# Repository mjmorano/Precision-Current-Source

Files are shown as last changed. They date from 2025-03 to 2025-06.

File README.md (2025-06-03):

# Overview
This is all of the design files and the code needed for my precision current source. The code for the microcontroller was made using the Arduino framework and PlatformIO so it's easy to modify and can be uploaded without neededing a programmer, just an Arduino. The serial interface features a few basic commands for setting the current and reading it back using the onboard ADC, as well as reading the internal temperature sensors. I added a lot of error checking to the firmware so it should be basically impossible to make the device do something that it shouldn't, and give the user feedback if their inputs are accepted or not. This design uses an external voltage source up to 100 volts, so it can be used with relatively high resistance loads. It is also suitable for high inductance loads, and has been verified stable into 250 mH. The KiCad folder contains all of the schematics and the .zip files with the gerbers needed to have the PCBs and the front panel manufactured. I have the front panels made as aluminum PCBs with no copper layers, which pretty much any manufacturer can do.

<p align="center">
  
  
  
</p>

# Stability Measurement
Since this is meant to be used for driving gradient and shim coils for long experimental runs, temperature stability is critical. To measure the stability I rented a Keysight 3458A and logged data for a week at maximum output current and the result can be seen in the plot below. Allan deviations for this data are also shown. The current stability could be further improved by using a different voltage reference, the LTZ1000A or LM399 for example, but these would come with a significant accuracy penalty. Of course the accuracy can be calibrated in software, but that requires the user to have a very good DMM and makes the assembly process more complicated. I tried to balance initial accuracy and temperature stability as much as possible.

<p align="center">
  
  
</p>

# Flashing the Firmware
To upload the program to the microcontroller, the Arduino bootloader needs to be burned. It's possible to buy the microcontroller with the bootloader already installed, but it's easy to do yourself. The best way to do this is in the Arduino IDE, and I'll outline how to do it with either an Uno or a Nano. First the ArduinoISP sketch needs to be uploaded to Arduino and can be found under the example sketches as shown below.

<p align="center">
 
</p>

Once it's uploaded connect the Arduino pins to the 6 pin header on the current source as follows:

  | Arduino | Current Source |
  |:-------:|:--------------:|
  |    10   |    RESET       |
  |    11   |    MOSI        |
  |    12   |    MISO        |
  |    13   |    SCK         |
  |    5V   |    5V          |
  |   GND   |    GND         |

Next under tools set the programmer to be "Arduino as ISP", then click burn bootloader. If everything is working right a message should pop up in the bottom right corner of the Arduino IDE saying "Burning bootloader...", followed by a message saying "Done burning bootloader."
<p align="center">
  
  
  
</p>

Now that the bootloader is burned open the Code/Microcontroller folder from the repo in VS Code, making sure to have the PlatformIO extension installed. After PlatformIO initializes select the port for the Arduino that was used to burn the bootloader in the bottom left, for me it was COM5.
<p align="center">
  
</p>

After this all that needs to be done is to click the upload button and the terminal should look like the below image.
<p align="center">
  
  
</p>

Now the device is ready to be connected over USB to a computer.

# Serial Interface
When the device is connected to the computer it should show up as a COM port in windows and a ttyUSB device on Linux. On Linux the device will need to be chmodded in order to connect to it using pyserial. Usually the FTDI drivers automatically download or are already installed, but if not they can be downloaded [here](https://ftdichip.com/drivers/vcp-drivers/). The interface uses eight data bits, no parity, and one stop bit at 115200 baud. On powerup the device does some self checks and looks to see if the optional tmp117 temperature sensor is present. After connecting to the serial interface two readlines need to be done, the first says whether the tmp117 is detected or not, and the second is for any detected errors. If the device detects no errors the second readline will return "Ready." Examples of how to use pyserial with the device are shown in the Code/Serial_Interface_Examples.py file. There are some other commands not shown there, but they won't really be used.

# Schematics
[Precision Current Source.pdf](https://github.com/user-attachments/files/20560946/Precision.Current.Source.pdf)

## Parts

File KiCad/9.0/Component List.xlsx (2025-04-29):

Item | Qty | Reference(s) | Value | Footprint | Digikey Part # | Manufacturer part #
1 | 3 | C201, C204, C213 | 10u 100V | SMD 6.3x7.7 | 732-865060845002CT-ND | 865061000000
2 | 15 | C202, C208, C209, C210, C211, C212, C302, C305, C306, C309, C310, C311, C312, C313, C314 | 100n 50V X7R | 0603 | 399-C0603C104K5RACTUCT-ND | C0603C104K5RACTU
3 | 10 | C203, C301, C401, C402, C403, C404, C405, C406, C407, C408 | 47u 35V | SMD 6.3x5.5 | 732-8508-1-ND | 865081000000
4 | 2 | C205, C207 | 100p 50V C0G | 0603 | 490-1427-1-ND | GRM1885C1H101JA01D
5 | 1 | C206 | 1u 100V Film | 2824 | 478-4539-1-ND | CB052E0105JBC
6 | 2 | C307, C308 | 20p 50V C0G | 0603 | 1276-1187-1-ND | CL10C200JB8NNNC
7 | 8 | D201, D202, D401, D402, D403, D404, D405, D406 | Schottky 40V | SOD-123F | B140S1F-7 | 31-B140S1F-7CT-ND
8 | 2 | D301, D302 | Dual LED | WP934MD | 754-2010-ND | WP934MD/LILGD
9 | 1 | F201 | Fuse Holder | 0031.7701.22 | 486-3856-1-ND | 0031.7701.22
10 | 1 | FB301 | 120 | 0603 | 490-5254-1-ND | BLM18KG121TN1D
11 | 1 | HS201 | 6396BG | 6396BG | 6396BG-ND | 6396BG
12 | 1 | HS202 | Heatsink | 577102B04000G | HS368-ND | 577102B04000G
13 | 1 | J201, J202, J203, J204 | Tab Connector | Through Hole | 36-1211-ND | 1211
14 | 1 | J301 | 6 Pin Header | 2x3 2.54 Through Hole | 952-2121-ND | M20-9980346
15 | 1 | J302 | USB B | Through Hole Right Angle | 102-3999-ND | UJ2-BH-1-TH
16 | 1 | Q201 | IRF510 | TO-220-3 | IRF510PBF-ND | IRF510PBF
17 | 1 | Q401 | FMMT614TA | SOT-23-3 | FMMT614CT-ND | FMMT614TA
18 | 1 | Q402 | FMMT734 | SOT-23-3 | FMMT734CT-ND | FMMT734TA
19 | 1 | R201 | 10K | 0603 | RMCF0603JT10K0CT-ND | RMCF0603JT10K0
20 | 6 | R202, R203, R303, R304, R305, R306 | 1k | 0603 | RMCF0603FT1K00CT-ND | RMCF0603FT1K00
21 | 1 | R204 | 10R | TO-220-4 | Y0926-10A-ND | Y092610R0000T9L
22 | 2 | R401, R402 | 160 | 603 | 311-160GRCT-ND | RC0603JR-07160RL
23 | 3 | RN301, RN302, RN303 | 4x1k | 4x0603 | 60-742C083102JPCT-ND | 742C083102JP
24 | 1 | RN304 | 4x120 | 4x0603 | Y4121CT-ND | EXB-V8V121JV
25 | 1 | S101 | RF Shield Frame | 32x32 | 903-BMI-S-204-FCT-ND | BMI-S-204-F
26 | 2 | TH301, TH302 | 1k NTC | Through Hole | 900-2152723107-ND | 2152723107
27 | 1 | U201 | ADR441B | SOIC-8 | 505-ADR441BRZ-ND | ADR441BRZ
28 | 1 | U202 | LTC1595B | SOIC-8 | LTC1595BCS8#TRPBFCT-ND | LTC1595BCS8#TRPBF
29 | 1 | U203 | OPA4182 | SOIC-14 | 296-OPA4182IDRCT-ND | OPA4182IDR
30 | 1 | U204 | AD7789 | MSOP-10 | AD7789BRMZ-REELCT-ND | AD7789BRMZ-REEL
31 | 1 | U205 | 4x1k | SOIC-8 | ORNT-1KACT-ND | ORNTA1001AT1
32 | 1 | U301 | FT231XS-U | SSOP-10 | 768-1156-5-ND | FT231XS-U
33 | 1 | U302 | ATMEGA328P | TQFP-32 | ATMEGA328P-AU-ND | ATMEGA328P-AU
34 | 1 | U303 | ADuM261N0 | SOIC-16 7.5W | 505-ADUM261N0BRIZ-ND | ADUM261N0BRIZ
35 | 1 | U304 | TMP117xxDRV | WSON-6 | 296-51835-1-ND | TMP117MAIDRVR
36 | 1 | U401 | L78L15 | SOT-89-3 | 497-7769-1-ND | L78L15ABUTR
37 | 1 | U402 | PESE1-S5-S24-M | SMD-10 Module | PESE1-S5-D24-M-TR | PESE1-S5-D24-M-TR
38 | 1 | U403 | L78L05 | SOT-89-3 | 497-1181-1-ND | L78L05ABUTR
39 | 1 | U404 | L79L15 | SOT-89-3 | 497-L79L15ACUCT-ND | L79L15ACUTR
40 | 1 | Y301 | 16 MHz | HC-49/US | XC1776CT-ND | ECS-160-20-3X-TR
Mechanical Parts
Item | Qty | Description | Digikey Part # | Manufacturer Part #
1 | 1 | RF Shield Cover | 903-1016-ND | BMI-S-204-C
2 | 1 | Terminal Block Header | 277-5988-ND | 707264
3 | 1 | Terminal Block | 277-1013-ND | 1757035
4 | 2 | Terminal Block Mounting Screw | 277-5786-ND | 708263
5 | 1 | Enclosure | HM972-ND | 1455K1201
6 | 8 | Crimp Connector | 277-17467-ND | 3240535
7 | 8 | 6-32x3/8" Screw | PMS 632 0038 PH | H356-ND
8 | 1 | 350 mA Fast Blow Fuse | 486-3000-ND | 3404.0043.11

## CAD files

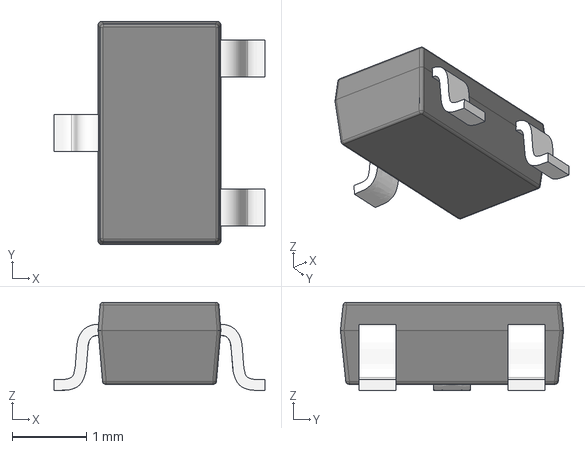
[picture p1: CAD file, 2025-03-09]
KiCad/9.0/3D Models/SOT23-3.stp
2.84 x 3.00 x 1.18 mm

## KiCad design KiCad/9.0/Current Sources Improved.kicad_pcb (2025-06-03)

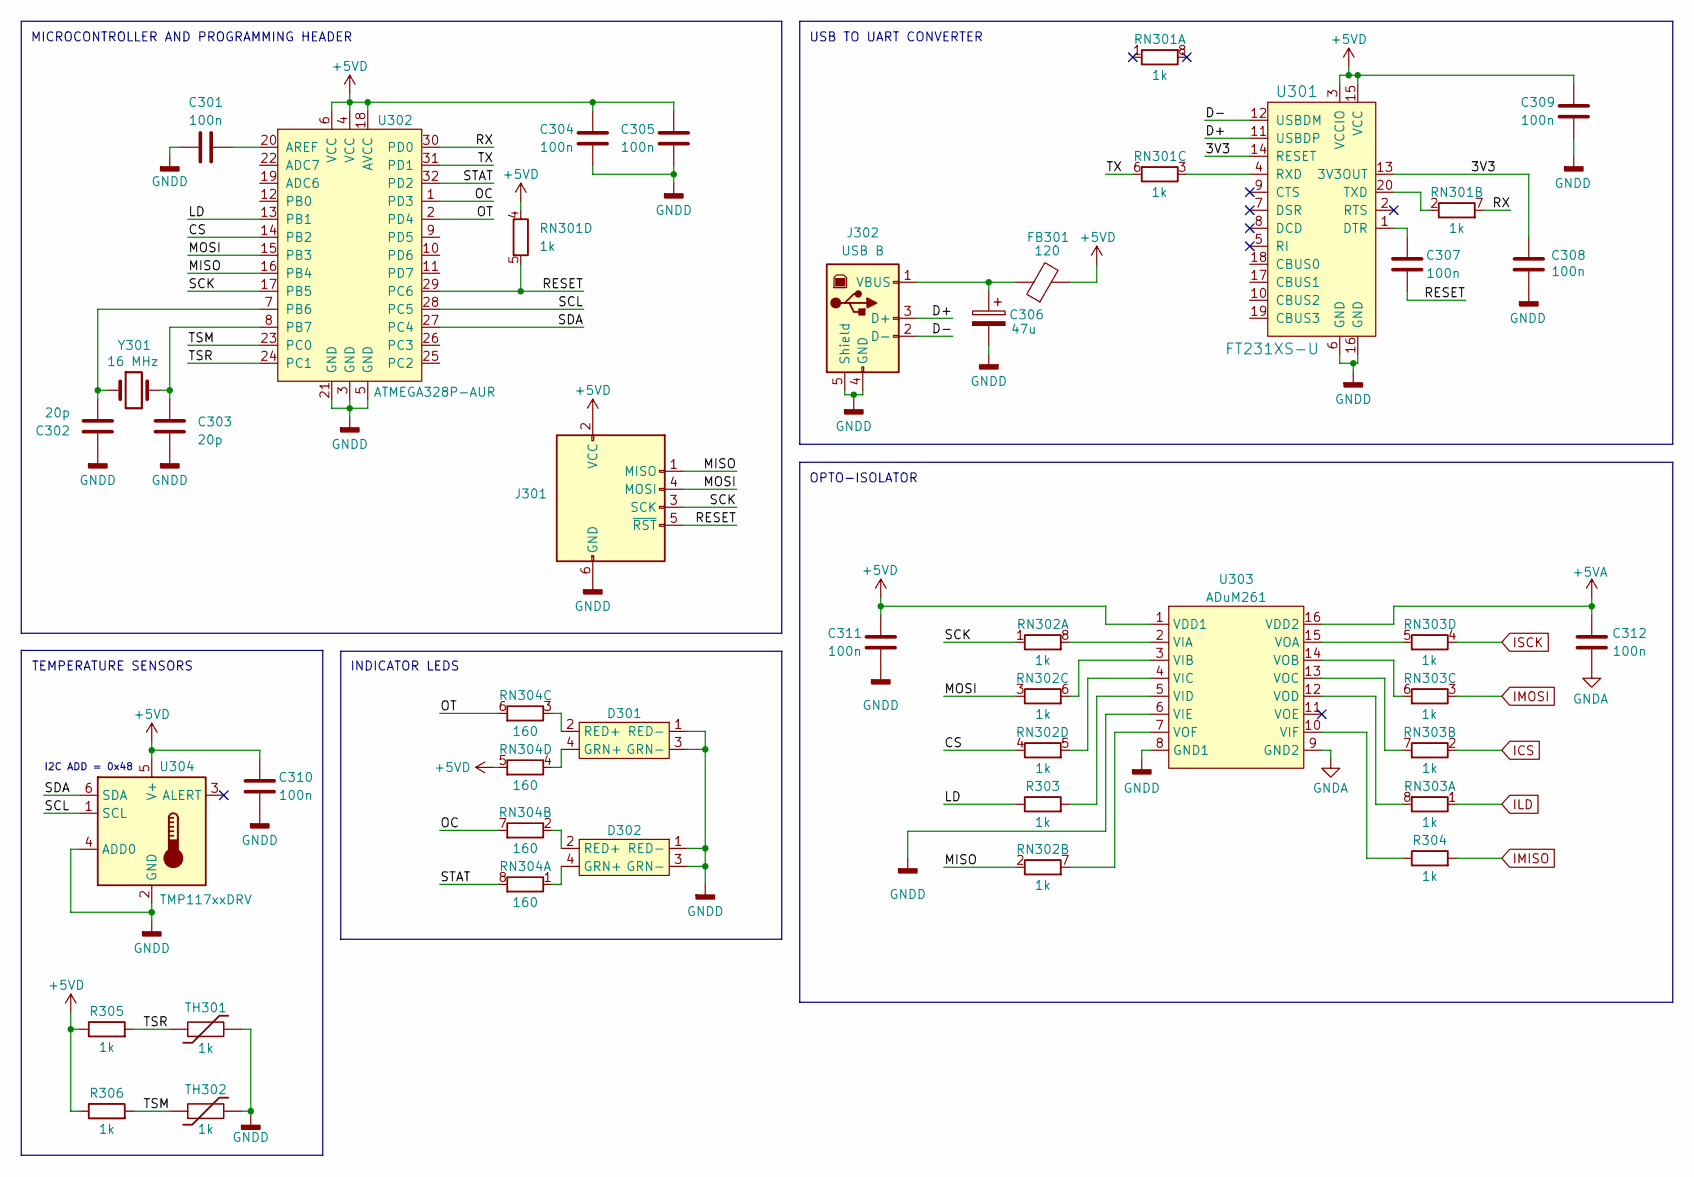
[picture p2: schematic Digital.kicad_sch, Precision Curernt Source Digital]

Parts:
C301, C304, C305, C307, C308, C309, C310, C311, C312: 100n; C_0603_1608Metric
C302, C303: 20p; C_0603_1608Metric
C306: 47u; CP_Elec_6.3x5.8
D301, D302: WP934MD
FB301: 120; R_0603_1608Metric
J301: AVR-ISP-6; PinHeader_2x03_P2.54mm_Vertical
J302: USB B; UJ2-BH-1-TH_CUD
R303, R304, R305, R306: 1k; R_0603_1608Metric
RN301, RN302, RN303: 1k; R_Array_Concave_4x0603
RN304: 160; R_Array_Concave_4x0603
TH301, TH302: 1k; PinHeader_1x02_P2.54mm_Vertical
U301: FT231XS-U; SSOP-20_W3.9mm; MPN FT231XS-U; Digi-Key_PN 768-1156-5-ND
U302: ATMEGA328P-AUR; TQFP-32_7x7mm; MPN ATMEGA328P-AUR; Digi-Key_PN ATMEGA328P-AURCT-ND
U303: ADuM261; SOIC-16W_7.5x12.8mm_P1.27mm
U304: TMP117xxDRV; WSON-6-1EP_2x2mm_P0.65mm_EP1x1.6mm
Y301: 16 MHz; XTAL_ECS-200-20-3X-TR

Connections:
+5VA: C312.2, U303.16 (VDD2); also elsewhere on the board
+5VD: C304.1, C305.2, C309.2, C310.1, C311.2, FB301.2, J301.2 (VCC), R305.1, R306.1, RN301.4 (R4.1), RN304.5 (R4.2), U301.3 (VCCIO), U301.15 (VCC), U302.4 (VCC), U302.6 (VCC), U302.18 (AVCC), U303.1 (VDD1), U304.5 (V+); also elsewhere on the board
/Digital/3V3: C308.1, U301.13 (3V3OUT), U301.14 (RESET)
/Digital/CS: RN302.4 (R4.1), U302.14 (PB2)
/Digital/D+: J302.3 (D+), U301.11 (USBDP)
/Digital/D-: J302.2 (D-), U301.12 (USBDM)
/Digital/LD: R303.1, U302.13 (PB1)
/Digital/MISO: J301.1 (MISO), RN302.2 (R2.1), U302.16 (PB4)
/Digital/MOSI: J301.4 (MOSI), RN302.3 (R3.1), U302.15 (PB3)
/Digital/OC: RN304.7 (R2.2), U302.1 (PD3)
/Digital/OT: RN304.6 (R3.2), U302.2 (PD4)
/Digital/RESET: C307.1, J301.5 (~RST), RN301.5 (R4.2), U302.29 (PC6)
/Digital/RX: RN301.7 (R2.2), U302.30 (PD0)
/Digital/SCK: J301.3 (SCK), RN302.1 (R1.1), U302.17 (PB5)
/Digital/SCL: U302.28 (PC5), U304.1 (SCL)
/Digital/SDA: U302.27 (PC4), U304.6 (SDA)
/Digital/STAT: RN304.8 (R1.2), U302.32 (PD2)
/Digital/TSM: R306.2, TH302.1, U302.23 (PC0)
/Digital/TSR: R305.2, TH301.1, U302.24 (PC1)
/Digital/TX: RN301.6 (R3.2), U302.31 (PD1)
GNDA: C312.1, U303.9 (GND2); also elsewhere on the board
GNDD: C301.2, C302.1, C303.2, C304.2, C305.1, C306.2, C308.2, C309.1, C310.2, C311.1, D301.1 (RED-), D301.3 (GRN-), D302.1 (RED-), D302.3 (GRN-), J301.6 (GND), J302.4 (GND), J302.5 (Shield), TH301.2, TH302.2, U301.6 (GND), U301.16 (GND), U302.3 (GND), U302.5 (GND), U302.21 (GND), U303.6 (VIE), U303.8 (GND1), U304.2 (GND), U304.4 (ADD0); also elsewhere on the board
ICS: RN303.2 (R2.1); also elsewhere on the board
ILD: RN303.1 (R1.1); also elsewhere on the board
IMISO: R304.2; also elsewhere on the board
IMOSI: RN303.3 (R3.1); also elsewhere on the board
ISCK: RN303.4 (R4.1); also elsewhere on the board
unnamed: D301.4 (GRN+), RN304.4 (R4.1)
unnamed: D301.2 (RED+), RN304.3 (R3.1)
unnamed: D302.4 (GRN+), RN304.1 (R1.1)
unnamed: D302.2 (RED+), RN304.2 (R2.1)
unnamed: C306.1, FB301.1, J302.1 (VBUS)
unnamed: RN301.2 (R2.1), U301.20 (TXD)
unnamed: RN301.3 (R3.1), U301.4 (RXD)
unnamed: RN302.8 (R1.2), U303.2 (VIA)
unnamed: RN302.7 (R2.2), U303.7 (VOF)
unnamed: RN302.6 (R3.2), U303.3 (VIB)
unnamed: RN302.5 (R4.2), U303.4 (VIC)
unnamed: RN303.8 (R1.2), U303.12 (VOD)
unnamed: RN303.7 (R2.2), U303.13 (VOC)
unnamed: RN303.6 (R3.2), U303.14 (VOB)
unnamed: RN303.5 (R4.2), U303.15 (VOA)
unnamed: C307.2, U301.1 (DTR)
unnamed: C301.1, U302.20 (AREF)
unnamed: C302.2, U302.7 (PB6), Y301.1
unnamed: C303.1, U302.8 (PB7), Y301.2
unnamed: R303.2, U303.5 (VID)
unnamed: R304.1, U303.10 (VIF)

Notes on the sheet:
MICROCONTROLLER AND PROGRAMMING HEADER
TEMPERATURE SENSORS
INDICATOR LEDS
USB TO UART CONVERTER
I2C ADD = 0x48
OPTO-ISOLATOR

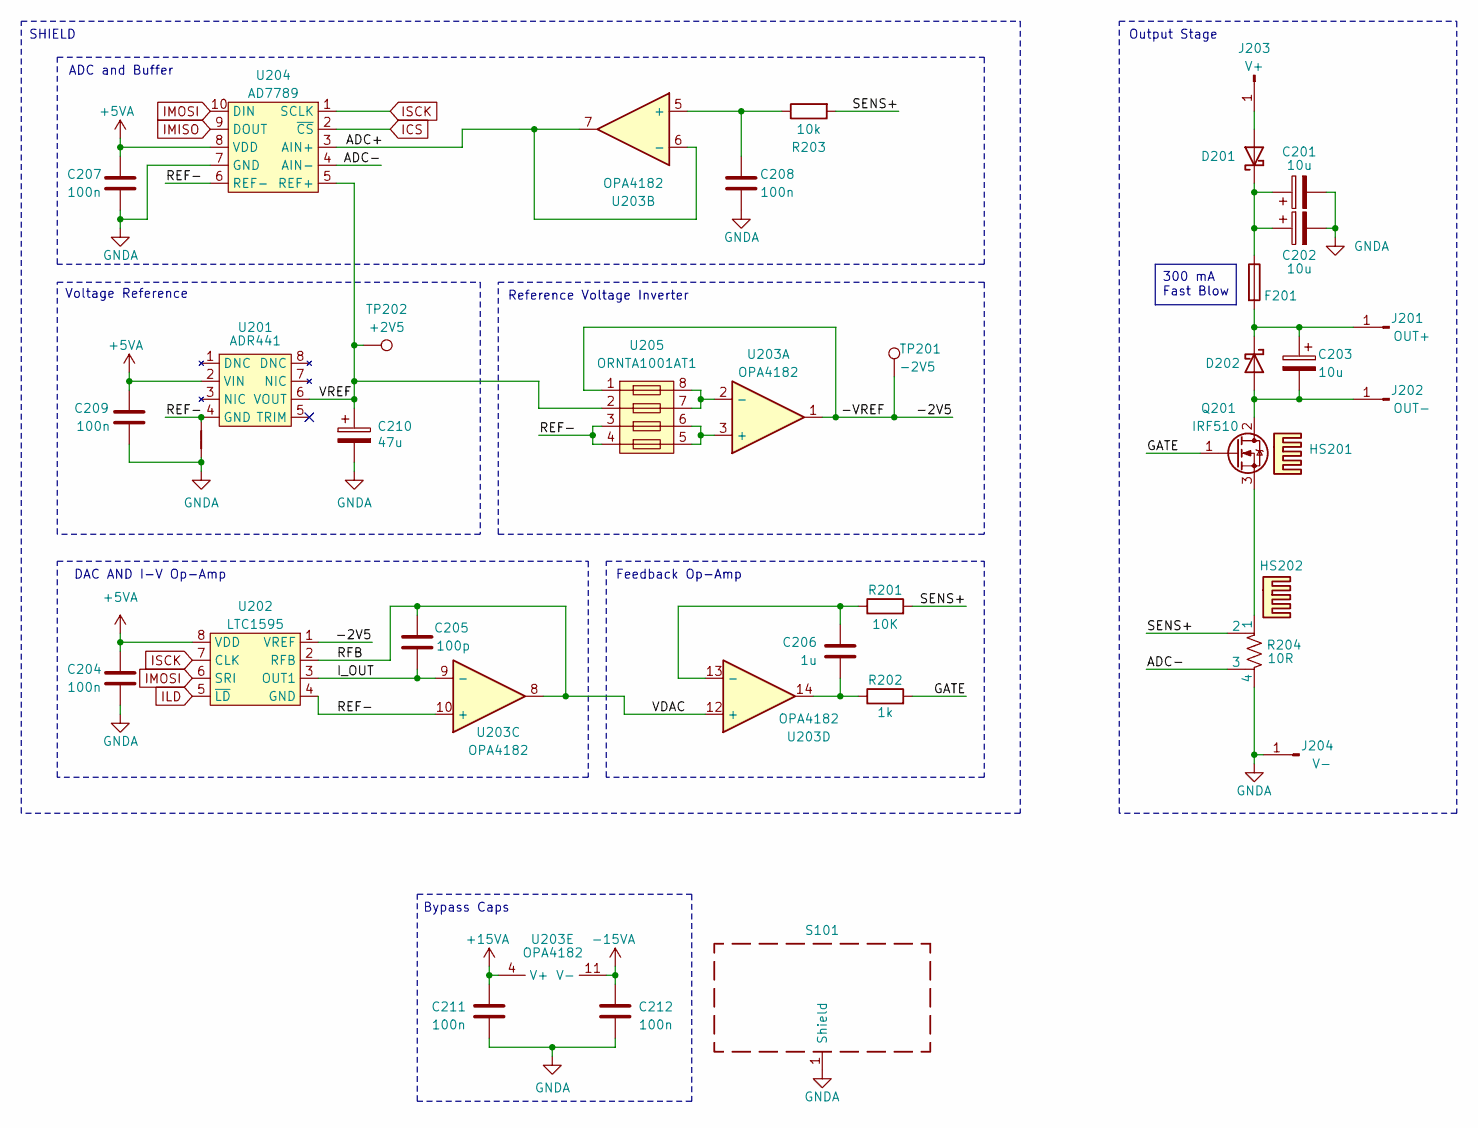
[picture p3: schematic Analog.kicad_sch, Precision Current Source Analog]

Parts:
C201, C202, C203: 10u; CP_Elec_6.3x5.8
C204, C207, C208, C209, C211, C212: 100n; C_0603_1608Metric
C205: 100p; C_0603_1608Metric
C206: 1u; CB05_AVX
C210: 47u; CP_Elec_6.3x5.8
D201, D202: D_Schottky; D_SOD-123F
F201: Fuse; 0031.7701.22
HS201: 530002B02500G; 529802B02500G; Mouser Part Number 532-530002B02500G
HS202: Heatsink; 577102B04000G
J201: OUT+; 1211
J202: OUT-; 1211
J203: V+; 1211
J204: V-; 1211
NT201: NetTie_2; SmallNetTie
Q201: IRF510; TO-220-3_Vertical
R201: 10K; R_0603_1608Metric
R202: 1k; R_0603_1608Metric
R203: 10k; R_0603_1608Metric
R204: 10R; TO-220-4_Vertical
S101: RFShield_OnePiece; Laird_Technologies_BMI-S-204-F_32.00x32.00mm
TP201: -2V5; TestPoint_Pad_D1.0mm
TP202: +2V5; TestPoint_Pad_D1.0mm
U201: ADR441; SOIC-8_3.9x4.9mm_P1.27mm
U202: LTC1595; SOIC-8_3.9x4.9mm_P1.27mm
U203: OPA4182; SOIC-14_3.9x8.7mm_P1.27mm
U204: AD7789; MSOP-10_3x3mm_P0.5mm
U205: ORNTA1001AT1; SOIC-8_3.9x4.9mm_P1.27mm

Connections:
+5VA: C204.1, C207.1, C209.1, U201.2 (VIN), U202.8 (VDD), U204.8 (VDD); also elsewhere on the board
+15VA: C211.2, U203.4 (V+); also elsewhere on the board
-15VA: C212.2, U203.11 (V-); also elsewhere on the board
/Analog/-2V5: TP201.1, U202.1 (VREF), U203.1, U205.1
/Analog/ADC+: U203.6 (-), U203.7, U204.3 (AIN+)
/Analog/ADC-: R204.3, U204.4 (AIN-)
/Analog/GATE: Q201.1 (G), R202.2
/Analog/I_OUT: C205.2, U202.3 (OUT1), U203.9 (-)
/Analog/REF-: NT201.2, U201.4 (GND), U202.4 (GND), U203.10 (+), U204.6 (REF-), U205.3, U205.4
/Analog/RFB: C205.1, U202.2 (RFB), U203.8, U203.12 (+)
/Analog/SENS+: R201.2, R203.2, R204.2
/Analog/VREF: C210.1, TP202.1, U201.6 (VOUT), U204.5 (REF+), U205.2
GNDA: C201.2, C202.2, C204.2, C207.2, C208.2, C209.2, C210.2, C211.1, C212.1, J204.1, NT201.1, R204.4, S101.1 (Shield), U204.7 (GND); also elsewhere on the board
ICS: U204.2 (~CS); also elsewhere on the board
ILD: U202.5 (~LD); also elsewhere on the board
IMISO: U204.9 (DOUT); also elsewhere on the board
IMOSI: U202.6 (SRI), U204.10 (DIN); also elsewhere on the board
ISCK: U202.7 (CLK), U204.1 (SCLK); also elsewhere on the board
unnamed 40: C206.2, R202.1, U203.14; also elsewhere on the board
unnamed: D201.2 (A), J203.1
unnamed: C201.1, C202.1, D201.1 (K), F201.1
unnamed: C203.2, D202.2 (A), J202.1, Q201.2 (D)
unnamed: C203.1, D202.1 (K), F201.2, J201.1
unnamed: Q201.3 (S), R204.1
unnamed: U203.3 (+), U205.5, U205.6
unnamed: U203.2 (-), U205.7, U205.8
unnamed: C208.1, R203.1, U203.5 (+)
unnamed 68: C206.1, R201.1, U203.13 (-); also elsewhere on the board

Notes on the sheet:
ADC and Buffer
SHIELD
Reference Voltage Inverter
Feedback Op-Amp
Voltage Reference
DAC AND I-V Op-Amp
Output Stage
Bypass Caps
300 mA Fast Blow

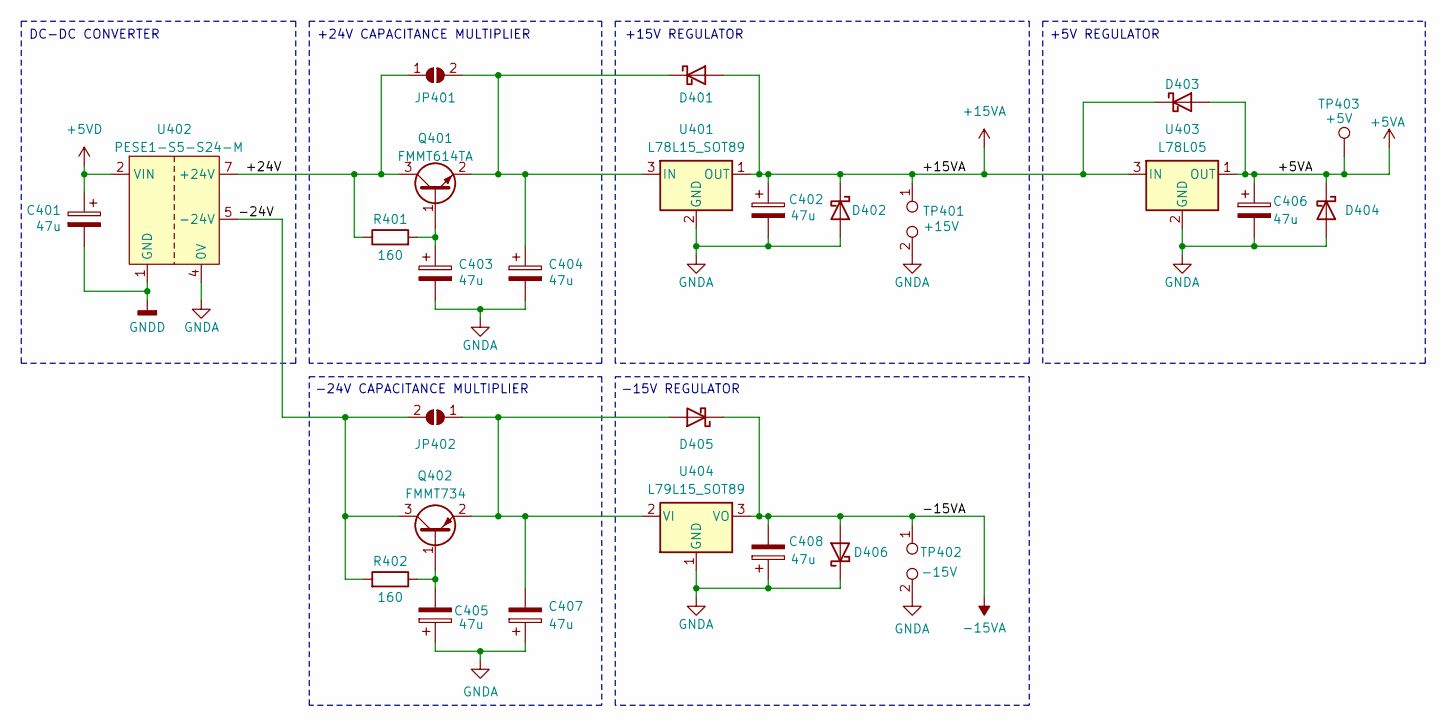
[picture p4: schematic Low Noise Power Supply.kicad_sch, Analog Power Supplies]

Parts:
C401, C402, C403, C404, C405, C406, C407, C408: 47u; CP_Elec_6.3x5.8
D401, D402, D403, D404, D405, D406: D_Schottky; D_SOD-123F
JP401, JP402: SolderJumper_2_Open; SolderJumper-2_P1.3mm_Open_RoundedPad1.0x1.5mm
Q401: FMMT614TA; SOT-23-3
Q402: FMMT734; SOT-23-3
R401, R402: 160; R_0603_1608Metric
TP401: +15V; testPoint2Pads
TP402: -15V; testPoint2Pads
TP403: +5V; TestPoint_Pad_D1.0mm
U401: L78L15_SOT89; SOT-89-3
U402: PESE1-S5-S24-M; PDS1-S5-D15-M-TR
U403: L78L05; SOT-89-3
U404: L79L15_SOT89; SOT-89-3

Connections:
+5VA: C406.1, D403.2 (A), D404.1 (K), TP403.1, U403.1 (OUT); also elsewhere on the board
+5VD: C401.1, U402.2 (VIN); also elsewhere on the board
+15VA: C402.1, D401.2 (A), D402.1 (K), D403.1 (K), TP401.1, U401.1 (OUT), U403.3 (IN); also elsewhere on the board
-15VA: C408.2, D405.1 (K), D406.2 (A), TP402.1, U404.3 (VO); also elsewhere on the board
/POWER/+24V: JP401.1 (A), Q401.3 (C), R401.1, U402.7 (+24V)
/POWER/-24V: JP402.2 (B), Q402.3 (C), R402.2, U402.5 (-24V)
GNDA: C402.2, C403.2, C404.2, C405.1, C406.2, C407.1, C408.1, D402.2 (A), D404.2 (A), D406.1 (K), TP401.2, TP402.2, U401.2 (GND), U402.4 (0V), U403.2 (GND), U404.1 (GND); also elsewhere on the board
GNDD: C401.2, U402.1 (GND); also elsewhere on the board
unnamed: C404.1, D401.1 (K), JP401.2 (B), Q401.2 (E), U401.3 (IN)
unnamed: C407.2, D405.2 (A), JP402.1 (A), Q402.2 (E), U404.2 (VI)
unnamed: C403.1, Q401.1 (B), R401.2
unnamed: C405.2, Q402.1 (B), R402.1

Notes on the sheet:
-24V CAPACITANCE MULTIPLIER
+24V CAPACITANCE MULTIPLIER
+5V REGULATOR
-15V REGULATOR
DC-DC CONVERTER
+15V REGULATOR

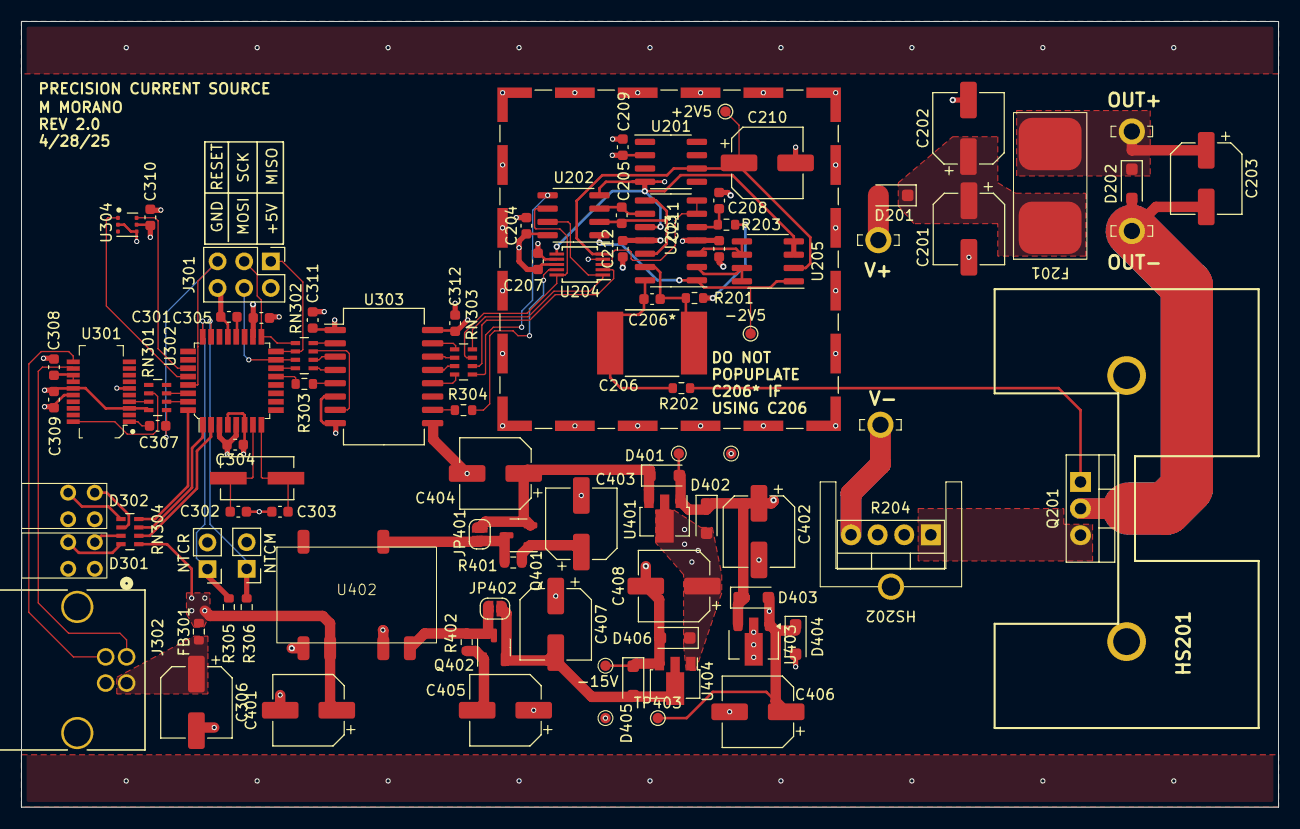
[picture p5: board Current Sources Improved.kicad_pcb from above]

Board: 4 copper layers, 120.0 x 75.0 mm, 95 parts (1 on the bottom side), 75 nets.

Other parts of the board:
C206*: C_0603_1608Metric

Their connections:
unnamed 40: C206*.1; also elsewhere on the board
unnamed 68: C206*.2; also elsewhere on the board

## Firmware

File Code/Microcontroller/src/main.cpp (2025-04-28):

/*
 * Code for the B0 and shim/gradient powIer supply. Uses an AD7789 ADC for current readback
 * and an LTC1595 based circuit for setting the output current. Uses a modified version of
 * the Analog Devices CN0216 circuit from the lab example for reading the ADC.
 * 
 * Author: M. Morano
 * Date: 4/25/2025
*/

#include <Arduino.h>
#include <SPI.h>
#include <Wire.h>
#include <Adafruit_TMP117.h>
#include <Adafruit_Sensor.h>
#include "AD7789.h"

// Do all the setup stuff
#define STAT 2      // Stats LED pin
#define OC 3        // Overcurrent LED pin
#define OT 4        // Overtemp LED pin
#define LD 9        // LD pin for the LTC1595
#define TSR A0      // Resistor NTC on ADC channel 0
#define TSM A1      // MOSFET NTC on ADC channel 1

const float maxAdcCode = pow(2, 24);        // Max code for 24 bit ADC
const float maxDacCode = pow(2, 16) - 1;    // Max code for 16 bit DAC
float R1 = 10.0f;                           // Current shunt resistor value. Change this if using different value
float vref = 2.5f;                          // ADC reference voltage
uint16_t code = 0;                          // Code for DAC current setpoint
float I = 0.0;                              // Current set value
uint32_t myTime = 0;                        // Used for polling the temperature sensors
uint8_t nAvg = 1;                           // Number of ADC averages
bool adcGood = false;

// Temperature sensor stuff
Adafruit_TMP117  tmp117;
sensors_event_t temp;
bool tmpFound = true;
float* Ta = &temp.temperature;
float Tr = 0.0f;                // NTC1 temperature reading
float Tm = 0.0f;                // NTC2 temperature reading
const float beta = 3892.0f;     // Beta value for NTC
float TaMax = 80.f;             // Maximum temperature for the enclosure before shutdown
float TrMax = 90.f;             // Maximum temperature for the feedback resistor before shutdown
float TmMax = 90.f;             // Maximum temperature for the MOSFET before shutdown

const char term = '\n';         // Terminator for serial interface

float read_ADC(){
  
  uint32_t reading = 0;
  uint32_t ui32status = 0;
  
  for(int i=0; i<nAvg; i++){
    
    ui32status = 0;
    
    do {
      ui32status = AD7789.readAD7789(STATUS_READ);
    } while (ui32status & 0x80);
    
    reading += AD7789.readAD7789(DATA_READ);
  }
  
  return ((float)reading / (float)nAvg) * vref / maxAdcCode / R1;
}

float read_ADC_VDD(){
  
  uint32_t reading = 0;
  uint32_t ui32status = 0;
    
  do {
    ui32status = AD7789.readAD7789(STATUS_READ_VDD);
  } while (ui32status & 0x80);
    
  reading += AD7789.readAD7789(DATA_READ);
  
  return 1.17f * 5.f * (float)reading / maxAdcCode;
}

void readTemps(){
  int sensorValue = analogRead(TSR);
  float RNTC = 1e3 / (1023.0 / sensorValue - 1);
  Tr = 1.f / ( 1.f / 298.15f + (1.f / beta) * (float)log(RNTC / 1e3f) ) - 273.25f; // Gives the temperature in celsius
  delay(1);
  sensorValue = analogRead(TSM);
  RNTC = 1e3 / (1023.0 / sensorValue - 1);
  Tm = 1.f / ( 1.f / 298.15f + (1.f / beta) * (float)log(RNTC / 1e3f) ) - 273.25f; // Gives the temperature in celsius
}

void writeDAC(uint16_t code){
  SPI.beginTransaction( SPISettings(1000000, MSBFIRST, SPI_MODE0) );
  SPI.transfer16(code);
  SPI.endTransaction();
  digitalWrite(LD, LOW);
  digitalWrite(LD, HIGH);
}

bool AD7789INIT(){
	AD7789.writeAD7789(RESET, 0xFF);		      // Resets the part for initial use
	delay(1000);
  AD7789.writeAD7789(COMM_WRITE_VDD, 0x00);
  AD7789.writeAD7789(MODE_WRITE_VDD, 0x06);	    // Mode register value (continuous conversion, unipolar input)
  float vdd = read_ADC_VDD();
  AD7789.writeAD7789(COMM_WRITE, 0x00);
  if(vdd >= 4.75f && vdd <= 5.25f)
    return true;
  else
    return false;
}

void parseCmd(String inString){

  int8_t index = inString.indexOf('?');

  if (index == -1){
    index = inString.indexOf('=');

    if (index == -1)
      Serial.println("Invalid syntax");

    else {
      char cmd[10];
      char value[10];
      char* end;
      sscanf(inString.c_str(), "%[^=]=%s", cmd, value);

      if (!strcmp(cmd, "code")){
        int32_t inInt = strtol(value, &end, 10);

        if (isControl(*end)){
          if (inInt >= 0 && inInt <= 65535){
            code = (uint16_t)inInt;
            writeDAC(code);
            Serial.println("Ok");

          } else
            Serial.println("Code must be between 0 and 65535");

        } else
          Serial.println("Invalid Code");

      } else if (!strcmp(cmd, "nAvg")){        
        int32_t inInt = strtol(value, &end, 10);       

        if (isControl(*end)){
          if (inInt >= 1 && inInt <= 255){
            nAvg = (uint8_t)inInt;
            Serial.println("Ok");

          } else 
            Serial.println("nAvg must be between 1 and 255");

        } else
            Serial.println("Invalid number");

      } else if (!strcmp(cmd, "curr")){
        float I = (float)strtod(value, &end);

        if (isControl(*end)){          
          if (I >= 0.f && I <= 0.25f){
            code = (uint16_t)(maxDacCode * R1 * I / vref);
            writeDAC(code);
            Serial.println("Ok");

          } else 
            Serial.println("Current must be between 0 and 250mA");

        } else 
          Serial.println("Invalid number");

      } else if (!strcmp(cmd, "TrMax")){        
        float limit = (float)strtod(value, &end);       

        if (isControl(*end)){
          if (limit >= 0.f && limit <= 100.f){
            TrMax = limit;
            Serial.println("Ok");

          } else 
            Serial.println("TrMax must be between 0 and 100 C");

        } else
            Serial.println("Invalid temperature");

      } else if (!strcmp(cmd, "TaMax")){        
        float limit = (float)strtod(value, &end);       

        if (isControl(*end)){
          if (limit >= 0.f && limit <= 100.f){
            TaMax = limit;
            Serial.println("Ok");

          } else 
            Serial.println("TaMax must be between 0 and 100 C");

        } else
            Serial.println("Invalid temperature");

      } else if (!strcmp(cmd, "TmMax")){        
        float limit = (float)strtod(value, &end);       

        if (isControl(*end)){
          if (limit >= 0.f && limit <= 100.f){
            TmMax = limit;
            Serial.println("Ok");

          } else 
            Serial.println("TmMax must be between 0 and 100 C");

        } else
            Serial.println("Invalid temperature");

      } else
        Serial.println("Invalid command");

    }

  } else {

    char cmd[10];
    sscanf(inString.c_str(), "%[^?]?", cmd);

    if (!strcmp(cmd, "max")){      
      Serial.println("250 mA");

    } else if (!strcmp(cmd, "curr")){
      Serial.println(read_ADC(), 7);

    } else if (!strcmp(cmd, "TaMax")){
      Serial.println(TaMax, 2);

    } else if (!strcmp(cmd, "TrMax")){
      Serial.println(TrMax, 2);

    } else if (!strcmp(cmd, "TmMax")){
      Serial.println(TmMax, 2);

    } else if (!strcmp(cmd, "Tr")){
      Serial.println(Tr, 2);

    } else if (!strcmp(cmd, "Tm")){
      Serial.println(Tm, 2);

    } else if (!strcmp(cmd, "Ta")){
      Serial.println(*Ta, 2);

    } else if (!strcmp(cmd, "code")){
      Serial.println(code);

    } else if (!strcmp(cmd, "nAvg")){
      Serial.println(nAvg);

    } else if(!strcmp(cmd, "ID")){
      Serial.println("Precision current source");

    } else if(!strcmp(cmd, "temp")){
      if (tmpFound){
        tmp117.getEvent(&temp);
        Serial.print(*Ta, 2);
        Serial.print(", ");
      }
      Serial.print(Tr, 2);
      Serial.print(", ");
      Serial.println(Tm, 2);

    } else if(!strcmp(cmd, "Vdd")){
      AD7789.writeAD7789(COMM_WRITE_VDD, 0x00);
      AD7789.writeAD7789(MODE_WRITE_VDD, 0x06);	    // Mode register value (continuous conversion, unipolar input)
      float vdd = read_ADC_VDD();
      Serial.println(vdd, 7);
      AD7789.writeAD7789(COMM_WRITE, 0x00);

    } else if(!strcmp(cmd, "adc")){
      adcGood = AD7789INIT();
      if (adcGood)
        Serial.println("Good");
      else
        Serial.println("Bad");

    } else 
      Serial.println("Invalid query");

  }

}

void errorState(){
  while (1)
  {
    digitalWrite(STAT, HIGH);
    delay(250);
    digitalWrite(STAT, LOW);
    delay(250);
  }
}

void setup(){
	
  // open digital communication protocols
  Serial.begin(115200);
  Serial.setTimeout(50);
  SPI.begin();

  // initialize pins
  pinMode(OT, OUTPUT);
  digitalWrite(OT, LOW);
  pinMode(OC, OUTPUT);
  digitalWrite(OC, LOW);
  pinMode(STAT, OUTPUT);
  digitalWrite(STAT, LOW);       
  digitalWrite(SS, HIGH);		  
  pinMode(LD, OUTPUT);                
  digitalWrite(LD, HIGH);
  
  writeDAC(0);

  if (!tmp117.begin()) {
    Serial.println("Failed to find TMP117 chip");
    tmpFound = false;
    temp.temperature = 0.f;
  } else {
    Serial.println("TMP117 Found");
    tmp117.getEvent(&temp);
  }

  // initialize AD7791
  adcGood = AD7789INIT();

  // Read NTC temperature sensors
  readTemps();

  if (adcGood && Tr < TrMax && Tm < TmMax && *Ta < TaMax){
    Serial.println("Ready.");
    digitalWrite(STAT, HIGH);

  } else if (!adcGood){
    Serial.println("Error: Check ADC or power supply.");
    digitalWrite(OT, HIGH);
    digitalWrite(OC, HIGH);
    errorState();

  } else if (Tr >= TrMax){
    Serial.println("Error: R1 overtemp at startup.");
    digitalWrite(OT, HIGH);
    errorState();

  } else if (Tm >= TmMax){
    Serial.println("Error: MOSFET overtemp at startup.");
    digitalWrite(OT, HIGH);
    errorState();

  } else if (*Ta > TaMax){
    Serial.println("Error: Ambient overtemp at startup.");
    digitalWrite(OT, HIGH);
    errorState();

  } else {
    Serial.println("Error: ");
    errorState();

  }

  myTime = millis();

}

void loop(){

  if (millis() >= myTime + 500UL){
    readTemps();
    if (tmpFound)
      tmp117.getEvent(&temp);
    else
      temp.temperature = 0.f;

    if (Tr >= TrMax || Tm >= TmMax || *Ta >= TaMax){
      writeDAC(0);
      digitalWrite(OT, HIGH);
      errorState();
    }
    myTime = millis();

  }

  if (Serial.available()){
    String cmd = Serial.readStringUntil(term);

    if (cmd == "")
      Serial.println("Did you forget the \\n?");
    else
      parseCmd(cmd);
    
  }
}

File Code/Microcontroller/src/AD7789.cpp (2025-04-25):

/*
  AD7789.cpp - 
*/

#include <Arduino.h>
#include <SPI.h>
#include "AD7789.h"

AD7789class AD7789;

uint32_t AD7789class::readAD7789 (uint8_t ui8address){
	uint8_t ui8AdcUpperCodes = 0;			// Data register bits 23-16
	uint8_t ui8AdcMiddleCodes = 0;			// Data register bits 15-8
	uint8_t ui8AdcLowerCodes = 0;			// Data register bits 7-0
	uint32_t ui32AdcCodes = 0;

  SPI.beginTransaction( SPISettings(1000000, MSBFIRST, SPI_MODE3) );

	if (ui8address == DATA_READ){	
		digitalWrite(SS,LOW);
		SPI.transfer(ui8address); 
		ui8AdcUpperCodes = SPI.transfer(0x00);			// Data register bits 23-16
		ui8AdcMiddleCodes = SPI.transfer(0x00);			// Data register bits 15-8
		ui8AdcLowerCodes = SPI.transfer(0x00);			// Data register bits 7-0
		digitalWrite(SS,HIGH);
		ui32AdcCodes = ((long)ui8AdcUpperCodes << 16) | ((long)ui8AdcMiddleCodes << 8) | ui8AdcLowerCodes;
	}
	else {
		digitalWrite(SS, LOW);
		SPI.transfer(ui8address); 
		ui8AdcLowerCodes = SPI.transfer(0x00);			// register read
		digitalWrite(SS, HIGH);	
		ui32AdcCodes = ((long)ui8AdcUpperCodes << 16) | ((long)ui8AdcMiddleCodes << 8) | ui8AdcLowerCodes;
	}

  	SPI.endTransaction();
	return ui32AdcCodes;

}

void AD7789class::writeAD7789 (uint8_t ui8address, uint8_t ui8value)
{
	SPI.beginTransaction( SPISettings(1000000, MSBFIRST, SPI_MODE3) );
    	
	if (ui8address != RESET && ui8address != COMM_WRITE && ui8address != COMM_WRITE_VDD){
		digitalWrite(SS,LOW);
		SPI.transfer(ui8address); 
		SPI.transfer(ui8value);
		digitalWrite(SS,HIGH);
	}
	else if (ui8address == COMM_WRITE){
		digitalWrite(SS,LOW);
		SPI.transfer(COMM_WRITE); 
		digitalWrite(SS,HIGH);		
	}
	else if (ui8address == COMM_WRITE_VDD){
		digitalWrite(SS,LOW);
		SPI.transfer(COMM_WRITE_VDD); 
		digitalWrite(SS,HIGH);		
	}
	else {
		digitalWrite(SS,LOW);
		SPI.transfer(ui8value);
		SPI.transfer(ui8value);
		SPI.transfer(ui8value);
		SPI.transfer(ui8value);
		digitalWrite(SS,HIGH);
	}

	SPI.endTransaction();

}

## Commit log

2025-04-28 Adjusted designators for NTCs
    [Current Sources Improved.kicad_pcb, Digital.kicad_sch]
2025-04-29 Updated some designators and added component list
    [Analog.kicad_sch, Component List.csv, Current Sources Improved.kicad_pcb, Digital.kicad_sch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]
2025-04-29 Changed part list to .xlsx so formatting would save
    [Component List.csv, Component List.xlsx]
2025-05-01 Cleaned up a few things
    [Analog.kicad_sch, Current Sources Improved.kicad_pcb, Current Sources Improved.kicad_sch, Digital.kicad_sch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]
2025-05-01 Added ibom overlay
    [Current Sources Improved.kicad_pcb]
2025-06-03 Updated KiCad project to version 9
    [1211.step, 6396BG.step, Analog.kicad_sch, BMI-S-204-F.stp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]
